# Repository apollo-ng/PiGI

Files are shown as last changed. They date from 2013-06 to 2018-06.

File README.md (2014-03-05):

# PiGI - A Raspberry Pi Geiger-Mueller Interface



The PiGI is built as a ready-to-go drop-in module for the Raspberry Pi to transform it
into a versatile geiger counter to measure/monitor radioactivity. It will generate the
required high voltage the counting tubes need to operate and it will safely invert the
counting impulses to a falling edge, detectable by a GPIO Pin on the PI. But it's also
designed in such a universal way in order to be  very hackable. Basically it can be
connected to any processing system that can detect falling edges like:

  * Arduino
  * ATMega
  * PIC
  * Other embedded Linux ARM/MIPS systems with GPIO Inputs (GNUBLIN, Netus G20 etc.)

## Specifications

  * 40x43mm board
  * Very low energy consumption (<2mA @ 0.09uSv/h local dose rate)
  * Cathode counting
  * Low BOM count / small footprint
  * Very cheap design: Prototype costs per board -> EUR15 / High Volume Production < 10 EUR
  * Dual stackable for low/high dosis counting with 2 tubes
  * Open-Source Hardware/Software

## Hardware

  * Schematics
  * Board designs
  * Released under CERN OHL 1.2



## Software

### Features ###

  * Live Status
  * Live (15min/60min/24h) Graphs
  * Analog gauge
  * Ion Trace Visualizer
  * History
  * Tick Simulator (For show and development)
  * Hardware RNG entropy generator
  * More to come
  * Released under GPL V3

### Screenshots ###

#### Main instrument panel

#### History instrument panel

#### Ion trace visualizer


## Website & Contact

[https://apollo.open-resource.org/lab:pigi](https://apollo.open-resource.org/lab:pigi)

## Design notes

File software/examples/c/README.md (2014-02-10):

# Software

This is only examples/prove-of-concept code which is
only left here as an example. The current softfware
implementation is found in ../pigid

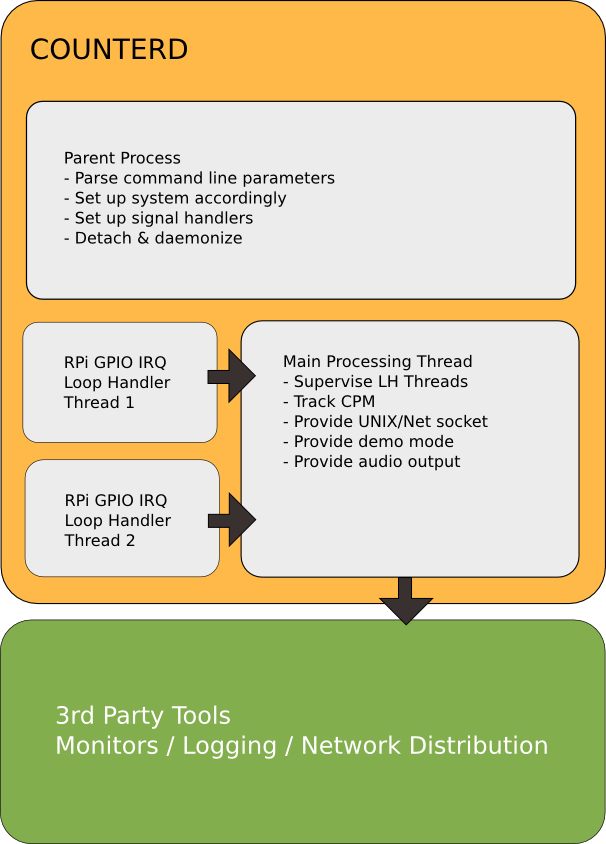
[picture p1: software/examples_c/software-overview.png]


This is how it should look like :)

## Basic software prove of concept

This is what is there for now.

### Compile

    gcc -o counterd counterd3.c

### Setup

Export the GPIO

    echo 4 > /sys/class/gpio/export
 
Set falling edge interrupt detection

    echo falling > /sys/class/gpio/gpio4/edge

Start the counter

    ./counterd

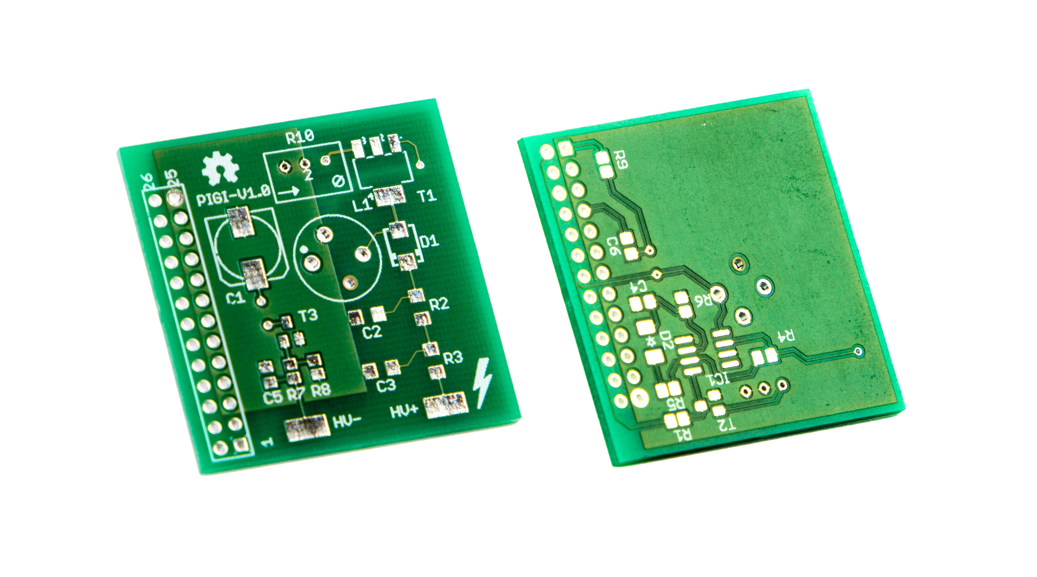
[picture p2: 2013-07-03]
hardware/PiGI-Prototype-Board-V1.0-PCB-only.jpg

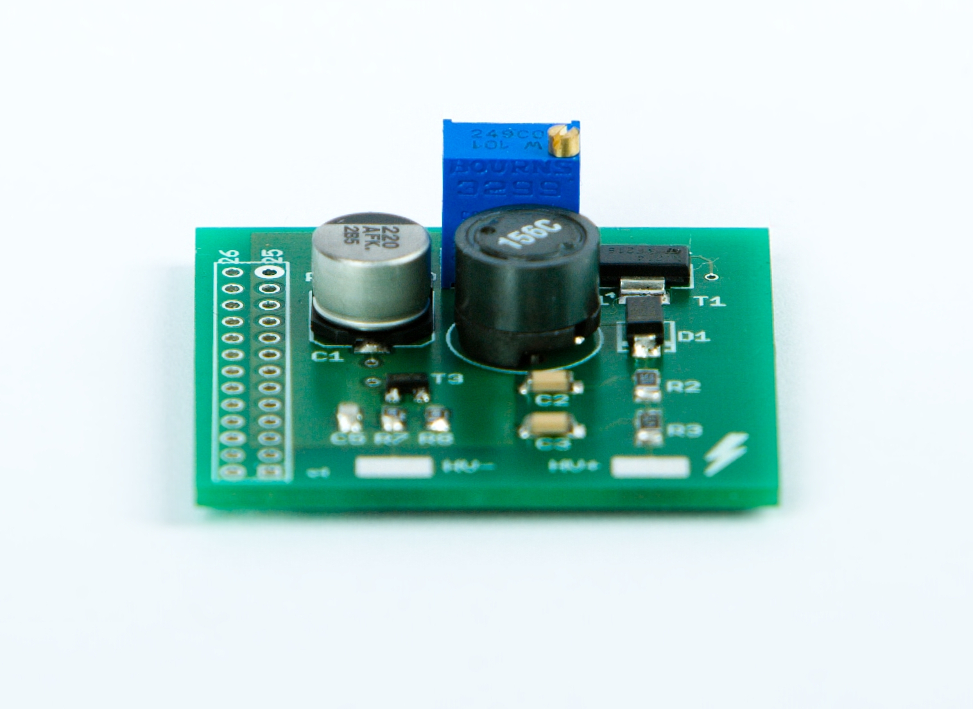
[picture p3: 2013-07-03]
hardware/PiGI-Prototype-Board-V1.0-perspective.jpg

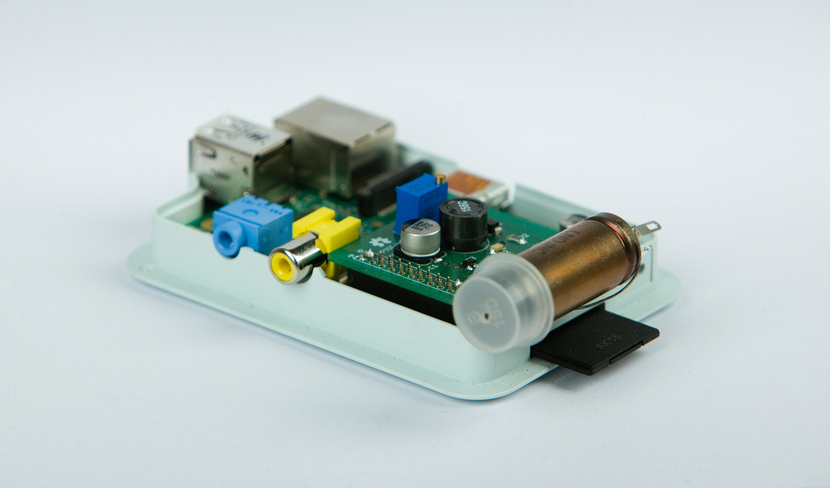
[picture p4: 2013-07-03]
hardware/PiGI-Prototype-Board-V1.0-on-Pi.jpg

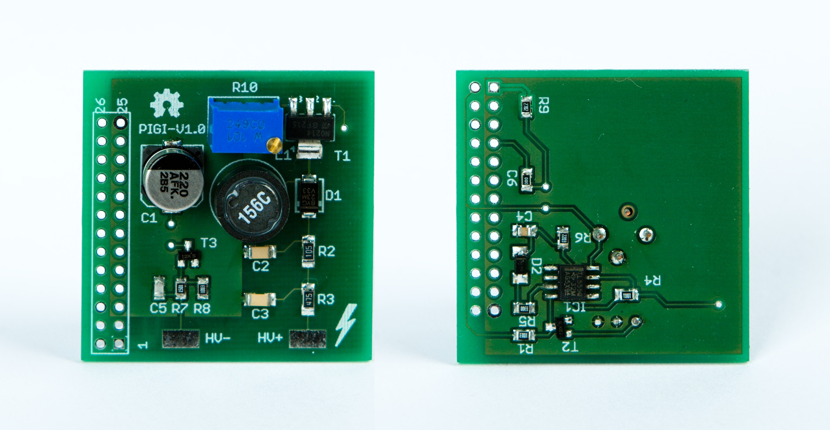
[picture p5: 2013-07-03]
hardware/PiGI-Prototype-Board-V1.0.jpg

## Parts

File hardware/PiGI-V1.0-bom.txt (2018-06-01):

Partlist exported from /home/chrono/eagle/PeIger-Counter/PiGI-V1.0.sch at 5/13/13 7:31 PM

Part      Value                  Device                 Package              Description                            
C1        220uF                  CPOL-EU153CLV-0810     153CLV-0810          POLARIZED CAPACITOR, European symbol   
C2        10nF/600               C-EUC1206              C1206                CAPACITOR, European symbol             
C3        10nF/600               C-EUC1206              C1206                CAPACITOR, European symbol             
C4        1nF                    C-EUC0805              C0805                CAPACITOR, European symbol             
C5        330p                   C-EUC0805              C0805                CAPACITOR, European symbol             
C6        100nF                  C-EUC0805              C0805                CAPACITOR, European symbol             
D1        UF4007                 MBRA340T3              SMA                  Surface Mount Schottky Power Rectifier 
D2        1N4148                 CGRM4001-G             SOD-123_MINI-SMA     Molded plasitc,JEDEC SOD-123/Mini SMA  
HV+       HV+                    SMD5                   SMD2,54-5,08         SMD PAD                                
HV-       HV-                    SMD5                   SMD2,54-5,08         SMD PAD                                
IC1       TLC555QDRQ1            TLC555QDRQ1            SO08                 TIMER                                  
L1        15mH                   1200LRS                1200LRS                                                     
LOGO1     OSHW_LOGO_FILLX0150-NT OSHW_LOGO_FILLX0150-NT OSHW_FILLX150_NOTEXT                                        
PIGI-V1.0 RASPBERRY-PI           RASPBERRY-PI           RASPBERRY-PI         Raspberry Pi Board                     
R1        100k                   R-EU_R0805             R0805                RESISTOR, European symbol              
R2        1M                     R-EU_R1206             R1206                RESISTOR, European symbol              
R3        4.7M                   R-EU_R1206             R1206                RESISTOR, European symbol              
R4        3.9k                   R-EU_M0805             M0805                RESISTOR, European symbol              
R5        330                    R-EU_R0805             R0805                RESISTOR, European symbol              
R6        220k                   R-EU_R0805             R0805                RESISTOR, European symbol              
R7        1.5k                   R-EU_R0805             R0805                RESISTOR, European symbol              
R8        100k                   R-EU_R0805             R0805                RESISTOR, European symbol              
R9        27k                    R-EU_R0805             R0805                RESISTOR, European symbol              
R10       100                    TRIM_EU-RJ9W           RJ9W                 POTENTIOMETER                          
T1        STN0214                -NPN-SOT223            SOT223               NPN Transistror                        
T2        2N4401                 NPN-TRANSISTOR_SOT23   SOT23                NPN TRANSISTOR                         
T3        2N4401                 NPN-TRANSISTOR_SOT23   SOT23                NPN TRANSISTOR

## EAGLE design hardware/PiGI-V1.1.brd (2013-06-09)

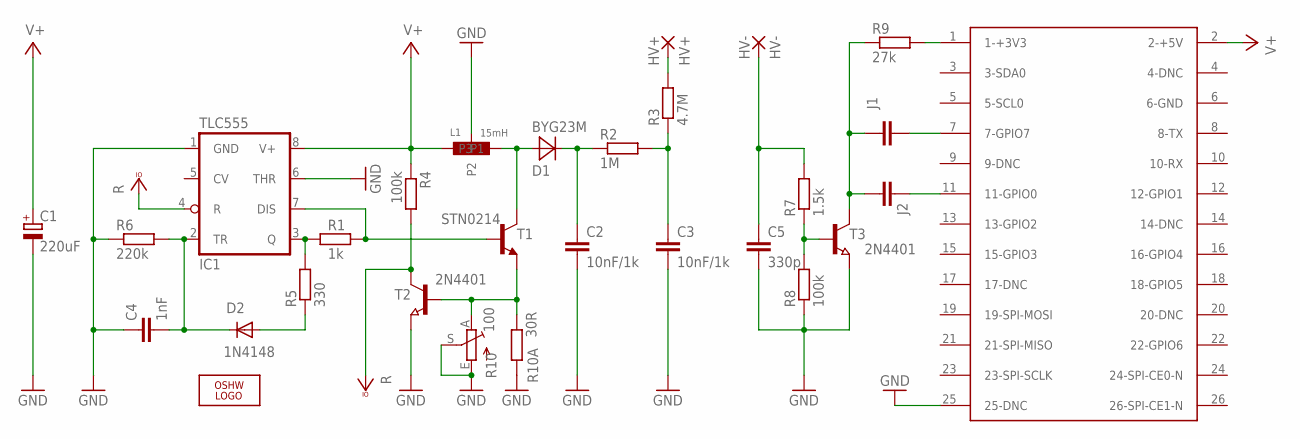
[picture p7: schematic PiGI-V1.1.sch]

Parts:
C1: 220uF; 153CLV-0810
C2, C3: 10nF/1k; C1206
C4: 1nF; C0805
C5: 330p; C0805
D1: BYG23M; SMA
D2: 1N4148; SOD-123_MINI-SMA
HV+: HV+; SMD2,54-5,08
HV-: HV-; SMD2,54-5,08
IC1: TLC555; SO08
J1, J2: C-EUC0805; C0805
L1: 15mH; 1200LRS
LOGO1: OSHW_LOGO_FILLX0150-NT; OSHW_FILLX150_NOTEXT
PI-GIV1.0: RASPBERRY-PI
R1: 1k; M0805
R2: 1M; R1206
R3: 4.7M; R1206
R4, R8: 100k; R0805
R5: 330; R0805
R6: 220k; R0805
R7: 1.5k; R0805
R9: 27k; R0805
R10: 100; RJ9W
R10A: 30R; M0805
T1: STN0214; SOT223
T2, T3: 2N4401; SOT23

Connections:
DIS: IC1.7 (DIS), R1.2, T1.1 (B)
GND: C1.-, C2.2, C3.2, C4.1, C5.2, IC1.1 (GND), IC1.6 (THR), L1.P4 (P2), PI-GIV1.0.25 (25-DNC), R6.1, R8.1, R10.E (A), R10.S, R10A.1, T2.2 (E), T3.2 (E)
unnamed: IC1.3 (Q), R1.1, R5.2
unnamed: D2.A, R5.1
unnamed: C2.1, D1.C, R2.1
unnamed: PI-GIV1.0.1 (1-+3V3), R9.2
unnamed: C4.2, D2.C, IC1.2 (TR), R6.2
unnamed: D1.A, L1.P3, T1.4 (C)
unnamed: R10.A (E), R10A.2, T1.3 (E), T2.1 (B)
unnamed: C3.1, R2.2, R3.1
unnamed: R7.1, R8.2, T3.1 (B)
unnamed: J1.2, J2.2, R9.1, T3.3 (C)
unnamed: C5.1, HV-.1, R7.2
unnamed: HV+.1, R3.2
unnamed: J1.1, PI-GIV1.0.7 (7-GPIO7)
unnamed: J2.1, PI-GIV1.0.11 (11-GPIO0)
V+: C1.+, IC1.8 (V+), L1.P1, PI-GIV1.0.2 (2-+5V), R4.1
VCCIO: IC1.4 (R), R4.2, T2.3 (C)

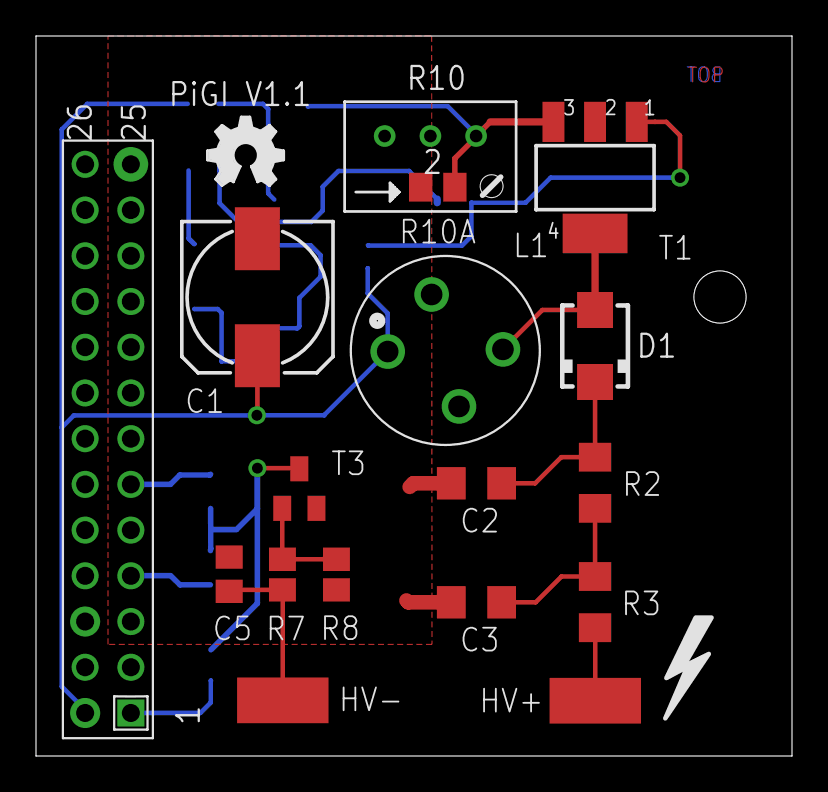
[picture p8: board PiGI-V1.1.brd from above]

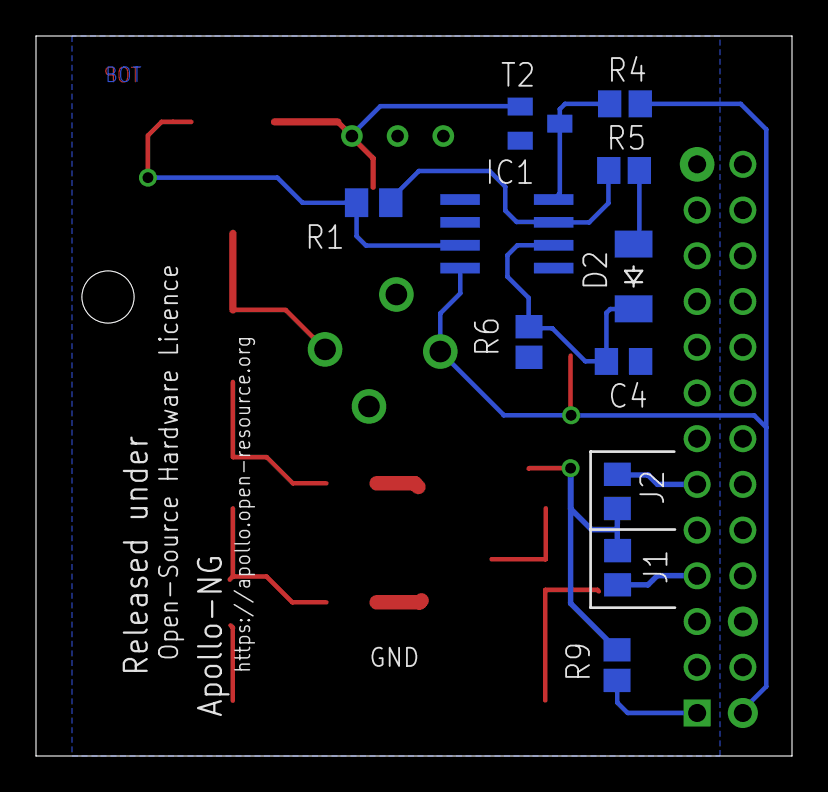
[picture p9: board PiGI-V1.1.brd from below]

Board: 2 copper layers, 42.0 x 40.0 mm, 29 parts (11 on the bottom side), 18 nets.

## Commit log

2013-06-08 Added V1.0 Board for the prototypes
    [PiGI-V1.0.brd, PiGI-V1.0.sch]
2013-06-08 Added V1.1 (pre-production state)
    [PiGI-V1.1.brd, PiGI-V1.1.sch]
2013-06-09 Minor position modifications of t/bnames placement on the board and clean up of schematics
    [PiGI-V1.1.brd, PiGI-V1.1.sch]
2013-06-23 Added HD images of prototype board V1.0
2014-02-09 webserver working again on non-pi devices
2014-02-10 refactoring to two sockets, audio toggle working again
2014-02-11 Updated README with current deps & install/usage instructions
2014-02-26 bugfix attempt for status socket
2014-03-04 Changed sample time of bell
2014-03-04 Fix for the fix for gevent-websocket-0.9.3 (current pip install). It worked well in tests with 0.3.6 however :/
2014-03-23 Increased multi device responsiveness of instrument-control
2014-03-25 Updated option_radio to device/browser independent/consistent styling
2014-03-26 Setting stage for gauges/status

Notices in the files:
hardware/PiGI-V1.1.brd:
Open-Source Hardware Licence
